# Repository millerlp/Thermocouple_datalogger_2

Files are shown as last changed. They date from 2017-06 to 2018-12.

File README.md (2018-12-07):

## Thermocouple_datalogger_2
### Luke Miller 2017

This repository contains code to run a 8-channel thermocouple
datalogger based on Arduino-type hardware. Currently there are 2 revisions,
A and B, which differ in the type of thermocouple-to-digital chip they use.
Revision A uses the older MAX31855K chip, while Revision B uses the more
recent MAX31856 that effectively superseded the MAX31855 series. Revision A
isn't recommended for new builds. 

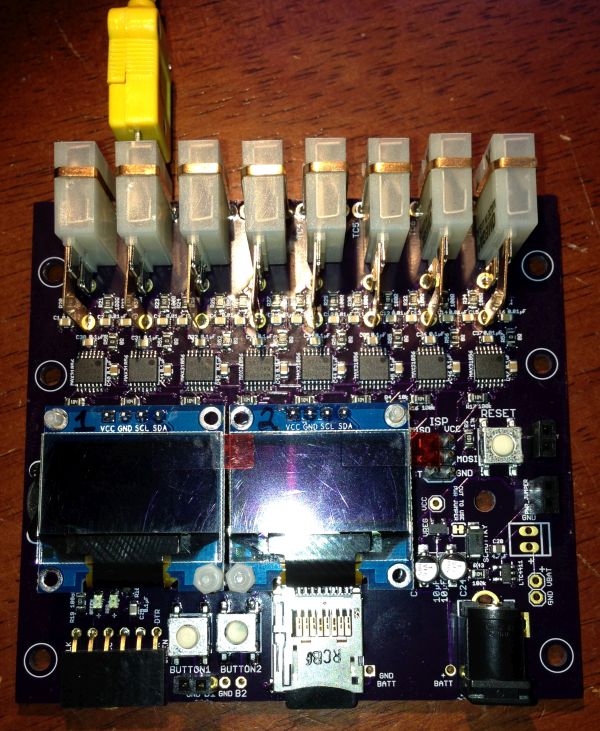
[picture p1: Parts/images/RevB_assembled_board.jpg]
Assembled RevB board


The directory `TempTracker` contains the primary files used to run a 
datalogger board, while the `testing` directory contains various utilities
used to test the basic functions of a datalogger board or to help calibrate
a board. 

## Required libraries:
* https://github.com/millerlp/TClib2
* https://github.com/millerlp/Adafruit_MAX31856 - fork of the original Adafruit_MAX31856 library, mainly changed to return NAN temperature values automatically if there is an error. 
* https://github.com/millerlp/RTClib - to run the onboard real time clock chip DS3231M
* https://github.com/greiman/SdFat - for reading/writing SD cards
* https://github.com/greiman/SSD1306Ascii - for writing to OLED displays

## Hardware designs

Eagle `.sch` and `.brd` design files are provided in the `Eagle_files` directory, along
with images of the designs. 

## Parts list

See the file `Thermocouple_datalogger_parts.xlsx` in the `Parts` directory for a 
list of all of the chips and other parts needed to build a board. There are 
separate sheets for Revision A and B, be careful to use the appropriate sheet. The 
majority of the parts should be available from a single vendor such as Digikey.com,
but the OLED display screens and thermocouple connectors need to be sourced 
elsewhere. 

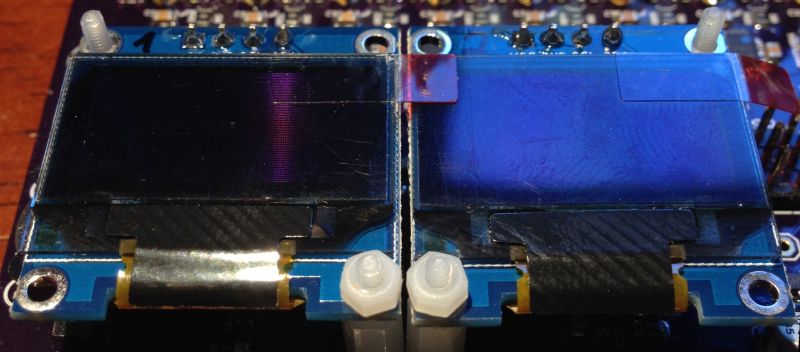
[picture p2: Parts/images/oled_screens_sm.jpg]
oled_screens_sm


For the OLED displays, any 128x64 pixel I2C SSD1306-based board should 
work (typically 0.96" size). These are available from several vendors on sites like
Amazon or Ebay. Be aware that there are I2C and SPI versions available, but this 
datalogger board will only communicate via I2C, so buying the 4-pin I2C version of the
display is sensible.

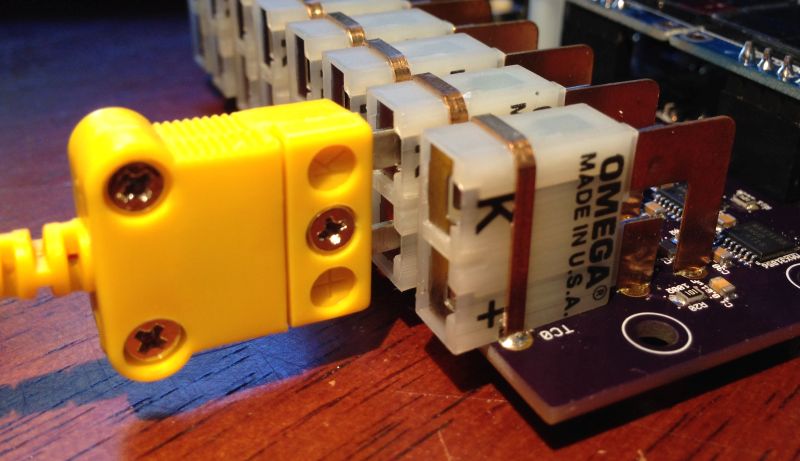
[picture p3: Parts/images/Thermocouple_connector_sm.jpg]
Thermocouple connector


The thermocouple "miniature" connectors will need to be sourced from a 
specialized vendor. The board is designed around Omega Engineering's PCC-SMP-V
connectors, which come in a minimum size batch of 5, so you'll need two batches to 
get 8. If you don't forsee needing to ever unplug a thermocouple, you could solder the
leads directly the board, forgoing the Omega connector. 

## Calibrating
The MAX3185x thermocouple chips are relatively accurate from the factory, and for
most purposes this will be sufficient, if you don't need absolute accuracy less than
1-2C. If you require sub-degree accurracy, calibration will be necessary, and this means
calibrating both the datalogger board and the individual thermocouple leads you use. 

Calibrating the datalogger board actually requires calibrating each of the 8 onboard 
MAX31856 chips separately, using a separate thermocouple calibrator such as the
Omega Engineering CL3515R. These devices are capable of outputting a millivolt signal
equivalent to what the relevant thermocouple type (K, T, J etc) would put out at a
specified temperature. The calibrator comes with a thermocouple cable that plugs 
directly into the thermocouple plugs on the datalogger board, mimicing a real 
thermocouple. The program `Calibration_routine_OLED_RevB` (or the RevA version) is meant
to be used with the external calibrator. After generating a set of calibration data for
a set of known temperatures, you can use the observed temperatures (recorded by the 
datalogger) and the known temperatures (from the calibrator) to fit a straight-line 
regression, and get the intercept (aka offset) and slope of the relationship between 
observed and expected readings. 

The program `Store_calibrations.ino` can then be used 
to upload the full set of 8 offset values and 8 slope values for the 8 MAX3185x 
chips to the datalogger's EEPROM onboard memory. The datalogger board will then have these
calibration values available to use every time it boots up. Typically I find that an 
individual MAX31855K or MAX31856 chip has a slope very near to 1.0 (ideal), but the 
intercept (aka offset) may often be +/- 0.5 to 1C off from ideal (0C offset). Therefore, calibration
is useful if you want the 8 individual channels on a board to be directly comparable to 
each other at the sub-degree level. The nominal temperature resolution of a MAX31855K chip is 0.25C (14-bit A-D converter) and the MAX31856 is 0.0078125 (19-bit A-D converter), but 
chip-to-chip variation from the factory can easily swamp that and only get you 
within +/- 2C of the true temperature in the normal biological range of temperatures. Careful calibration and housing the datalogger board in a thermally stable container 
should get you within 0.1C across channels. 

## Several words about the housing and thermal stability

The thermocouple-to-digital chips rely on an internal temperature sensor in the chip
itself to measure the "cold junction" temperature. This temperature is ideally equivalent
to the temperature at the point where the thermocouple plugs into the board and makes 
the transition from special thermocouple wire to the plain copper of the circuit board
(which is a thermocouple junction by definition). An accurate measurement of the 
distant ("hot") end of the thermocouple probe relies on the MAX3185x chip also knowing 
what the cold junction temperature is quite accurately. If the MAX3185x chip internal
temperature is a few degrees different than the thermocouple plug on the board, the
registered thermocouple temperature will also be off. Ideally, a block of material
that is thermally conductive (an "isothermal block") would be used to connect all 8 
of the MAX3185x chips and their respective thermocouple plugs, and thus keep all of 
those points at the same temperature. A bar of aluminum, copper, or brass, mounted so that 
it sits across the top of all the MAX3185x chips and also rests against the 
thermocouple plug terminals would be best, although these should not all be in 
electrical contact. To thermally couple the various parts without creating short 
circuits, adhesive thermal gap filler (often used to attach heat sinks to circuit 
boards and chips) can be used. This material is electrically non-conductive, but does
a reasonable job of allowing heat to transfer across it, and has the added benefit of
filling small gaps that might exist between an isothermal block and the various parts
due to height differences or variation in how flat the chips sit on the board. The RevB
board has two holes on the edges of the board positioned to help bolt an isothermal 
block across the tops of the MAX31856 chips. 

After provisioning an isothermal block, it would also be useful to then enclose the 
datalogger board in a housing that will stay relatively temperature-stable, or at 
least won't change temperature rapidly at different places. Surrounding the board in
insulating styrofoam may be desirable, and then placing that inside a plastic or metal housing that only exposes the front of the thermocouple connectors to the outside air. 
The RevB board is designed so that panel-mount buttons can be attached to wire leads and 
plugged into the board (via standard 0.1" headers), so that the buttons can be
mounted to a housing. The 2 OLED displays can be attached via 4-wire cables in the 
same manner. The rear/bottom edge of the board (opposite the thermocouple connectors) will 
need to be accessible through a housing wall so that the serial port, micro SD card slot, 
and 2.1mm DC power plug are accessible.

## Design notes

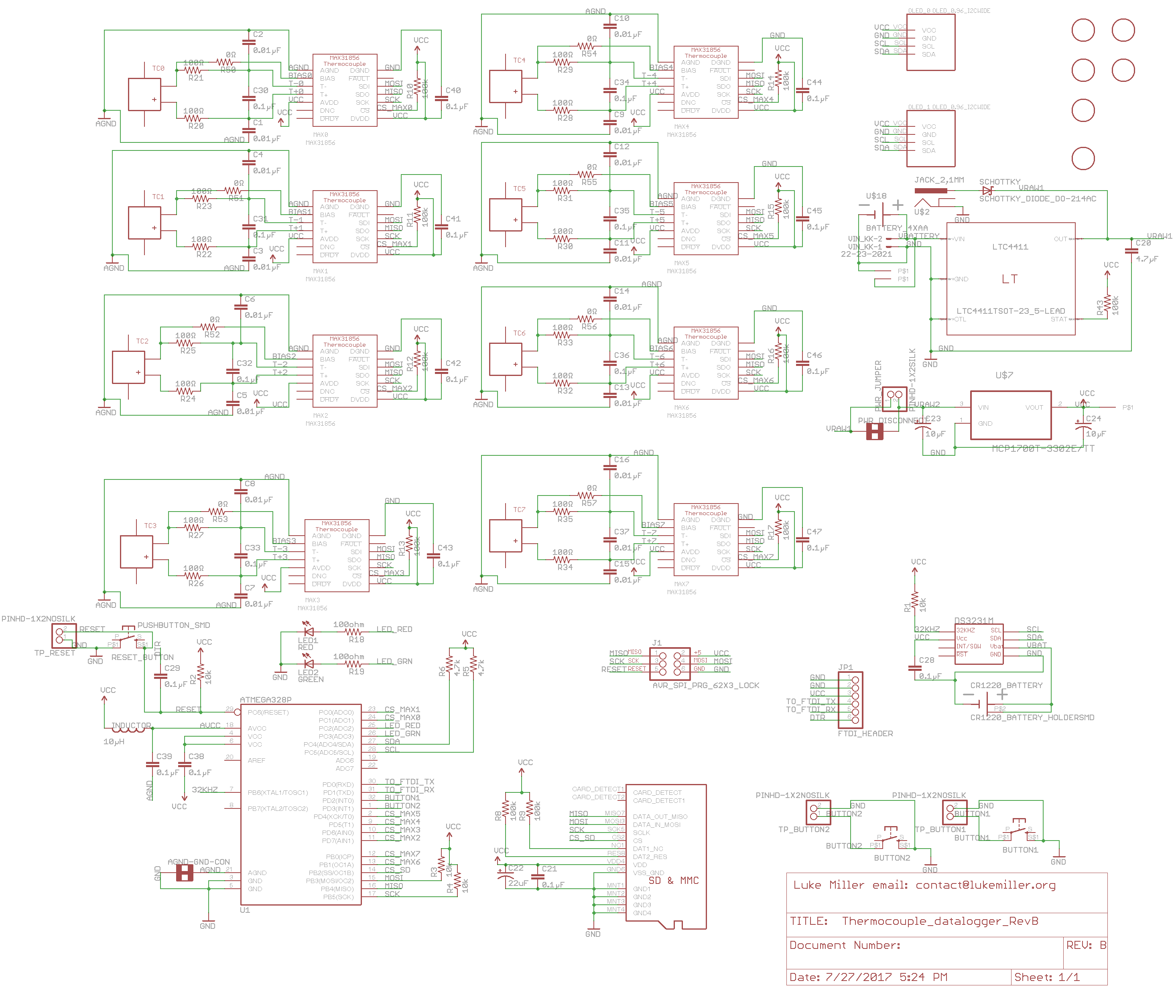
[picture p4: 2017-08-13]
Eagle_files/RevB/Thermocouple_datalogger_RevB_schematic.png

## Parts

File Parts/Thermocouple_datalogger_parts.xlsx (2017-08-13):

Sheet: Thermocouple_datalogger_RevA
Part Description | Eagle library part | Manufacturer | Mfr. PN | Quantity (for 1 board) | Digikey PN | Digikey $ | Extended $
Capacitor, surface mount 10uF 35V, electrolytic, Panasonic FC series, size code B | miller.lbr\CPOL-USB | Panasonic | EEE-FC1C100R | 2 | PCE3995CT-ND | $0.32 | $0.64
Capacitor, 0603 0.01µF 16V ceramic (10000pF) | miller.lbr\CAP0805 | KEMET | C0603C103K4RACTU | 8 | 399-7841-1-ND | $0.28 | $2.24
Capacitor, 0603 0.1µF 16V ceramic | miller.lbr\CAP0805 | KEMET | C0603C104K4RACTU | 13 | 399-1096-1-ND | $0.10 | $1.30
Capacitor, 22µF 6.3V 20% 0805 | miller.lbr\CPOL-US0805 | AVX Corporation | F920J226MPA | 1 | 478-8119-1-ND | $0.43 | $0.43
Resistor, 0603 100ohm | miller.lbr\RESISTOR_SMD | Yageo | RC0603JR-07100RL | 2 | 311-100GRCT-ND | $0.10 | $0.20
Resistor, 0603 10 k ohm | miller.lbr\RESISTOR_SMD | Yageo | RC0603JR-0710KL | 4 | 311-10KGRCT-ND | $0.10 | $0.40
Resistor, 0603 100 k ohm | miller.lbr\RESISTOR_SMD | Yageo | RC0603JR-07100KL | 10 | 311-100KGRCT-ND | $0.10 | $1.00
Screw terminal 2-position, through-hole | miller.lbr\TERMINAL-2PIN-2.54MM | On Shore Technologies | OSTVN02A150 | 2 | ED10561-ND | $0.58 | $1.16
LED, Red 0805 | miller.lbr\LED | Lite-On | LTST-C171KRKT | 1 | 160-1427-1-ND | $0.31 | $0.31
LED, Green 0805 | miller.lbr\LED | Lite-On | LTST-C171GKT | 1 | 160-1423-1-ND | $0.29 | $0.29
MAX31855K thermocouple convertor | miller.lbr\MAX31855 | Maxim Integrated | MAX31855KASA+ | 8 | MAX31855KASA+-ND | $4.50 | $36.00
Pushbutton switch SPST tactile, SMD | miller.lbr\PUSHBUTTON_DPST_SMD | Omron | B3S-1000P | 3 | SW836CT-ND | $0.82 | $2.46
Real Time Clock, DS3231M | miller.lbr\DS3231M | Maxim Integrated | DS3231MZ/V+ | 1 | DS3231MZ/V+-ND | $6.46 | $6.46
CR1220 Battery holder | miller.lbr\CR1220_BATTERY_HOLDER | Keystone | 3000 | 1 | 36-3000-ND | $0.58 | $0.58
CR1220 Battery, lithium |  | Energizer | CR1220VP | 1 | N033-ND | $0.95 | $0.95
4x1 Pin header, female, through hole | miller.lbr\PINHD-1x4BIG_LOCK | Sullins | PPTC041LFBN-RC | 1 | S7002-ND | $0.60 | $0.60
40x1 Pin header, male breakaway |  | Sullins | PRPC040SAAN-RC | 1 | S1011EC-40-ND | $0.74 | $0.74
2x1 Molex KK male connector, through hole | miller.lbr\22-23-2021 | Molex | 22-23-2021 | 1 | WM4200-ND | $0.16 | $0.16
2x1 Molex KK female connector |  | Molex | 10-11-2023 | 1 | WM2601-ND | $0.17 | $0.17
Molex KK crimp-on connector, 24-30AWG |  | Molex | 469990101 | 2 | WM5268-ND | $0.23 | $0.46
Inductor, 10µH 150mA, 360 mOhm | miller.lbr\INDUCTOR0805 | Taiyo-Yuden | LBR2012T100K | 1 | 587-2045-1-ND | $0.11 | $0.11
3x2 Pin header | miller.lbr\AVR_SPI_PRG_6 | Molex | 901310763 | 1 | WM8139-ND | $1.38 | $1.38
Voltage regulator MCP-1700T-3302 3.3V | miller.lbr\MCP1700T-3302E/TT | Microchip | MCP1700T-3302E/TT | 1 | MCP1700T3302ETTCT-ND | $0.38 | $0.38
MicroSD card slot push-push | miller.lbr\MICROSD_MOLEX_REVERSECURRENT | Molex | 5027740891 | 1 | WM24066CT-ND | $3.64 | $3.64
ATmega328P 32-TQFP | miller.lbr\ATMEGA328_SMT | Microchip | ATMEGA328P-AU | 1 | ATMEGA328P-AU-ND | $2.07 | $2.07
2.1mm Power jack | miller.lbr\POWER_JACK_2,1MM | CUI | PJ-202AH | 1 | CP-202AH-ND | $0.74 | $0.74
Ferrite 300 ohm 100Mhz 0805 | miller.lbr\FERRITE_BEAD | TDK | MMZ2012R301AT000 | 16 | 445-2191-1-ND | $0.11 | $1.76
 |  |  |  |  |  | Total | $66.63
Omega miniature thermocouple terminal vertical (5 pack) | miller.lbr\PCC-SMP-THERMOCOUPLE | Omega Engineering | PCC-SMP-V | 2 |  | $21.25 | $42.50

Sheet: Thermocouple_datalogger_RevB
Part Description | Eagle library part | Manufacturer | Mfr. PN | Quantity (for 1 board) | Digikey PN | Digikey $ | Extended $
Capacitor, surface mount 10uF 35V, electrolytic, Panasonic FC series, size code B | miller.lbr\CPOL-USB | Panasonic | EEE-FC1C100R | 2 | PCE3995CT-ND | $0.32 | $0.64
Capacitor, 0805 0.01µF 16V ceramic (10000pF) | miller.lbr\CAP0805 | KEMET | C0809C103K4RACTU | 17 | 399-7995-1-ND | $0.28 | $4.76
Capacitor, 0805 0.1µF 16V ceramic | miller.lbr\CAP0805 | KEMET | C0805C104K4RACTU | 20 | 399-1167-1-ND | $0.12 | $2.40
Capacitor, 0805 4.7µF 25V ceramic X5R | miller.lbr\CAP0805 | KEMET | C0805C475K3PACTU | 1 | 399-5505-1-ND | $0.33 | $0.33
Capacitor, 22µF 6.3V 20% 0805 tantalum | miller.lbr\CPOL-US0805 | AVX Corporation | F920J226MPA | 1 | 478-8119-1-ND | $0.43 | $0.43
Resistor, 0805 0 ohm (jumper) | miller.lbr\RESISTOR_SMD | Yageo | RC0805JR-070RL | 8 | 311-0.0ARCT-ND | $0.10 | $0.80
Resistor, 0805 100ohm 1/8watt | miller.lbr\RESISTOR_SMD | Yageo | RC0805JR-07100RL | 18 | 311-100ARCT-ND | $0.10 | $1.80
Resistor, 0805 4.7k ohm 1/8watt | miller.lbr\RESISTOR_SMD | Yageo | RC0805JR-074K7L | 2 | 311-4.7KARCT-ND | $0.10 | $0.20
Resistor, 0805 10 k ohm 1/8watt | miller.lbr\RESISTOR_SMD | Yageo | RC0805JR-0710KL | 4 | 311-10KARCT-ND | $0.10 | $0.40
Resistor, 0805 100 k ohm 1/8watt | miller.lbr\RESISTOR_SMD | Yageo | RC0805JR-07100KL | 11 | 311-100KARCT-ND | $0.10 | $1.10
LED, Red 0805 | miller.lbr\LED | Lite-On | LTST-C171KRKT | 1 | 160-1427-1-ND | $0.31 | $0.31
LED, Green 0805 | miller.lbr\LED | Lite-On | LTST-C171GKT | 1 | 160-1423-1-ND | $0.29 | $0.29
MAX31856 Thermocouple convertor | miller.lbr\MAX31856 | Maxim Integrated | MAX31856MUD+ | 8 | MAX31856MUD+-ND | $4.41 | $35.28
Pushbutton switch SPST tactile, SMD | miller.lbr\PUSHBUTTON_DPST_SMD | Omron | B3S-1000P | 3 | SW836CT-ND | $0.82 | $2.46
Real Time Clock, DS3231M | miller.lbr\DS3231M | Maxim Integrated | DS3231MZ/V+ | 1 | DS3231MZ/V+-ND | $6.46 | $6.46
CR1220 Battery holder | miller.lbr\CR1220_BATTERY_HOLDER | Keystone | 3000 | 1 | 36-3000-ND | $0.58 | $0.58
CR1220 Battery, lithium |  | Energizer | CR1220VP | 1 | N033-ND | $0.95 | $0.95
4x1 Pin header, female, through hole | miller.lbr\PINHD-1x4BIG_LOCK | Sullins | PPTC041LFBN-RC | 1 | S7002-ND | $0.60 | $0.60
40x1 Pin header, male breakaway |  | Sullins | PRPC040SAAN-RC | 1 | S1011EC-40-ND | $0.74 | $0.74
2x1 Molex KK male connector, through hole | miller.lbr\22-23-2021 | Molex | 22-23-2021 | 1 | WM4200-ND | $0.16 | $0.16
2x1 Molex KK female connector |  | Molex | 10-11-2023 | 1 | WM2601-ND | $0.17 | $0.17
Molex KK crimp-on connector, 24-30AWG |  | Molex | 469990101 | 2 | WM5268-ND | $0.23 | $0.46
Inductor, 10µH 150mA, 360 mOhm | miller.lbr\INDUCTOR0805 | Taiyo-Yuden | LBR2012T100K | 1 | 587-2045-1-ND | $0.11 | $0.11
3x2 Pin header | miller.lbr\AVR_SPI_PRG_6 | Molex | 901310763 | 1 | WM8139-ND | $1.38 | $1.38
Voltage regulator MCP-1700T-3302 3.3V | miller.lbr\MCP1700T-3302E/TT | Microchip | MCP1700T-3302E/TT | 1 | MCP1700T3302ETTCT-ND | $0.38 | $0.38
MicroSD card slot push-push | miller.lbr\MICROSD_MOLEX_REVERSECURRENT | Molex | 5027740891 | 1 | WM24066CT-ND | $3.64 | $3.64
ATmega328P 32-TQFP | miller.lbr\ATMEGA328_SMT | Microchip | ATMEGA328P-AU | 1 | ATMEGA328P-AU-ND | $2.07 | $2.07
2.1mm Power jack | miller.lbr\POWER_JACK_2,1MM | CUI | PJ-202AH | 1 | CP-202AH-ND | $0.74 | $0.74
Schottky diode 20V 1A | miller.lbr\SCHOTTKY_DIODE_DO-214AC | Vishay Semiconductor | SS12-E3/61T | 1 | SS12-E3/61TGICT-ND | $0.40 | $0.40
AA battery holder 4xAA, through hole | miller.lbr\BATTERY_4XAA | Keystone | 2477 | 1 | 36-2477-ND | $2.23 | $2.23
Power path controller LTC4411 TSOT-23 | miller.lbr\LTC4411TSOT-23_5-LEAD | Linear Technology | LTC4411ES5 | 1 | LTC4411ES5#TRMPBFCT-ND | $3.88 | $3.88
 |  |  |  |  |  | Digikey Total | $76.15
Other Vendors
Omega miniature thermocouple terminal vertical (5 pack) | miller.lbr\PCC-SMP-THERMOCOUPLE | Omega Engineering | PCC-SMP-V | 2 |  | $21.25 | $42.50
OLED 0.96" I2C screen 128x64 4pin | miller.lbr\OLED_0.96_I2CWIDE | Amazon HiLetgo | 3-01-1234-IIC-W | 2 | http://a.co/hNL97jw | $8.88 | $17.76

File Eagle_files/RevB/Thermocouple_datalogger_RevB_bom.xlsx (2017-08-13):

Qty | Value | Device | Parts
2 |  | PUSHBUTTON_DPST_SMDSTANDARD | BUTTON1, BUTTON2
17 | 0.01µF | CAP0805 | C1, C2, C3, C4, C5, C6, C7, C9, C10, C11, C12, C13, C14, C15, C16, C17, C37
20 | 0.1µF | CAP0805 | C30, C31, C32, C33, C34, C35, C36, C40, C41, C42, C43, C44, C45, C46, C47, C48, C49, C51, C52, C54
8 | 0O | RESISTOR_SMDR0805 | R7, R24, R27, R30, R33, R36, R39, R42
11 | 100k | RESISTOR_SMDR0805 | R10, R11, R12, R13, R14, R15, R16, R17, R18, R19, R43
2 | 100ohm | RESISTOR_SMDR0805 | R8, R9
16 | 100O | RESISTOR_SMDR0805 | R5, R6, R22, R23, R25, R26, R28, R29, R31, R32, R34, R35, R37, R38, R40, R41
4 | 10k | RESISTOR_SMDR0805 | R1, R2, R20, R21
2 | 10µF | CPOL-USB | C23, C24
1 | 10µH | INDUCTOR0805_TY | INDUCTOR
1 | 22-23-2021 | 22-23-2021 | VIN_KK
1 | 22uF | CPOL-US0805 | C8
2 | 4.7k | RESISTOR_SMDR0805 | R3, R4
1 | 4.7µF | CAP0805 | C18
1 | ATMEGA328P | ATMEGA328_SMT | U1
1 | AVR_SPI_PRG_62X3_LOCK | AVR_SPI_PRG_62X3_LOCK | J1
1 | BATTERY_4XAA | BATTERY_4XAA | U$18
1 | CR1220_BATTERY_HOLDERSMD | CR1220_BATTERY_HOLDERSMD | CR1220_BATTERY
1 | DS3231MSOIC-8 | DS3231MSOIC-8 | DS3231M
1 | FTDI_HEADER | PINHD-1X6RA | JP1
1 | GREEN | LED0805 | LED2
6 | HOLE-LAYOUT4-40-SOCKET-HEAD | HOLE-LAYOUT4-40-SOCKET-HEAD | U$6, U$15, U$16, U$23, U$24, U$25
1 | JACK_2,1MM | POWER_JACK_2,1MM | U$2
1 | LTC4411TSOT-23_5-LEAD | LTC4411TSOT-23_5-LEAD | LTC4411
8 | MAX31856 | MAX31856 | MAX0, MAX1, MAX2, MAX3, MAX4, MAX5, MAX6, MAX7
1 | MCP1700T-3302E/TT | MCP1700T-3302E/TT | U$7
1 | MICROSD_MOLEX_REVERSECURRENT | MICROSD_MOLEX_REVERSECURRENT | U$5
2 | OLED_0.96_I2CWIDE | OLED_0.96_I2CWIDE | OLED_0, OLED_1
8 | PCC-SMP-THERMOCOUPLEVERTICAL | PCC-SMP-THERMOCOUPLEVERTICAL | TC0, TC1, TC2, TC3, TC4, TC5, TC6, TC7
3 | PINHD-1X1STANDARD | PINHD-1X1STANDARD | TP_GND, TP_VBAT, VCC
3 | PINHD-1X2NOSILK | PINHD-1X2NOSILK | TP_BUTTON1, TP_BUTTON2, TP_RESET
1 | PUSHBUTTON_SMD | PUSHBUTTON_DPST_SMDSTANDARD | RESET_BUTTON
1 | RED | LED0805 | LED1
1 | SCHOTTKY_DIODE_DO-214AC | SCHOTTKY_DIODE_DO-214AC | SCHOTTKY
1 | SOLDER_JUMPER_TRACESTANDARD | SOLDER_JUMPER_TRACESTANDARD | AGND-GND-CON

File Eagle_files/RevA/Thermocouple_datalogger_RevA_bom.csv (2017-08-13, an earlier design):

Thermocouple_datalogger_RevA 2017-06-01
Part | Value | Device | Package | Description
AGND-GND-CON | SOLDER_JUMPER_TRACESTANDARD | SOLDER_JUMPER_TRACESTANDARD | SJ_2S-TRACE | Solder jumper with trace
BUTTON1 |  | PUSHBUTTON_DPST_SMDSTANDARD | PUSHBUTTON_DPST_SMD | PUSHBUTTON DPST SMD
BUTTON2 |  | PUSHBUTTON_DPST_SMDSTANDARD | PUSHBUTTON_DPST_SMD | PUSHBUTTON DPST SMD
C8 | 22uF | CPOL-US0805 | C0805_POL | POLARIZED CAPACITOR, American symbol
C23 | 10µF | CPOL-USB | PANASONIC_B | POLARIZED CAPACITOR, American symbol
C24 | 10µF | CPOL-USB | PANASONIC_B | POLARIZED CAPACITOR, American symbol
C30 | 0.01µF | CAP0805 | 805 | Capacitor
C31 | 0.01µF | CAP0805 | 805 | Capacitor
C32 | 0.01µF | CAP0805 | 805 | Capacitor
C33 | 0.01µF | CAP0805 | 805 | Capacitor
C34 | 0.01µF | CAP0805 | 805 | Capacitor
C35 | 0.01µF | CAP0805 | 805 | Capacitor
C36 | 0.01µF | CAP0805 | 805 | Capacitor
C37 | 0.01µF | CAP0805 | 805 | Capacitor
C40 | 0.1µF | CAP0805 | 805 | Capacitor
C41 | 0.1µF | CAP0805 | 805 | Capacitor
C42 | 0.1µF | CAP0805 | 805 | Capacitor
C43 | 0.1µF | CAP0805 | 805 | Capacitor
C44 | 0.1µF | CAP0805 | 805 | Capacitor
C45 | 0.1µF | CAP0805 | 805 | Capacitor
C46 | 0.1µF | CAP0805 | 805 | Capacitor
C47 | 0.1µF | CAP0805 | 805 | Capacitor
C48 | 0.1µF | CAP0805 | 805 | Capacitor
C49 | 0.1µF | CAP0805 | 805 | Capacitor
C51 | 0.1µF | CAP0805 | 805 | Capacitor
C52 | 0.1µF | CAP0805 | 805 | Capacitor
C54 | 0.1µF | CAP0805 | 805 | Capacitor
CR1220_BATTERY | CR1220_BATTERY_HOLDERSMD | CR1220_BATTERY_HOLDERSMD | CR1220_BATTERY_HOLDER_SMD | CR1220 Battery Holder
DIGITAL_OUTPUT_0 | TERMINAL-2PIN-2.54MM | TERMINAL-2PIN-2.54MM | TERMINAL-2PIN-2.54MM | Terminal block 0.1 spacing"
DIGITAL_OUTPUT_1 | TERMINAL-2PIN-2.54MM | TERMINAL-2PIN-2.54MM | TERMINAL-2PIN-2.54MM | Terminal block 0.1 spacing"
DS3231M | DS3231MSOIC-8 | DS3231MSOIC-8 | DS3231M_SOIC8 | DS3231M real time clock
INDUCTOR | 10µH | INDUCTOR0805_TY | I_0805 | Inductor
J1 | AVR_SPI_PRG_62X3_LOCK | AVR_SPI_PRG_62X3_LOCK | 2X3_LOCK | AVR ISP 6 Pin
JP1 | FTDI_HEADER | PINHD-1X6LOCK | 1X06-BIGLOCK | PIN HEADER
LED1 | RED | LED0805 | CHIPLED_0805 | LEDs
LED2 | GREEN | LED0805 | CHIPLED_0805 | LEDs
MAX0 | MAX31855 | MAX31855 | SO08 | MAX31855 Thermocouple amplifier with cold junction compensation, SPI communication
MAX1 | MAX31855 | MAX31855 | SO08 | MAX31855 Thermocouple amplifier with cold junction compensation, SPI communication
MAX2 | MAX31855 | MAX31855 | SO08 | MAX31855 Thermocouple amplifier with cold junction compensation, SPI communication
MAX3 | MAX31855 | MAX31855 | SO08 | MAX31855 Thermocouple amplifier with cold junction compensation, SPI communication
MAX4 | MAX31855 | MAX31855 | SO08 | MAX31855 Thermocouple amplifier with cold junction compensation, SPI communication
MAX5 | MAX31855 | MAX31855 | SO08 | MAX31855 Thermocouple amplifier with cold junction compensation, SPI communication
MAX6 | MAX31855 | MAX31855 | SO08 | MAX31855 Thermocouple amplifier with cold junction compensation, SPI communication
MAX7 | MAX31855 | MAX31855 | SO08 | MAX31855 Thermocouple amplifier with cold junction compensation, SPI communication
OLED_0 | OLED_0.96_I2CVCC_PIN1 | OLED_0.96_I2CVCC_PIN1 | OLED_0.96_I2C_VCC_PIN1 | CHECK VCC & GND PIN VARIANT
OLED_1 | OLED_0.96_I2CVCC_PIN1 | OLED_0.96_I2CVCC_PIN1 | OLED_0.96_I2C_VCC_PIN1 | CHECK VCC & GND PIN VARIANT
R1 | 10k | RESISTOR_SMDR0805 | R0805 | RESISTOR, American symbol
R2 | 10k | RESISTOR_SMDR0805 | R0805 | RESISTOR, American symbol
R3 | 10k | RESISTOR_SMDR0805 | R0805 | RESISTOR, American symbol
R4 | 10k | RESISTOR_SMDR0805 | R0805 | RESISTOR, American symbol
R8 | 100ohm | RESISTOR_SMDR0805 | R0805 | RESISTOR, American symbol
R9 | 100ohm | RESISTOR_SMDR0805 | R0805 | RESISTOR, American symbol
R10 | 100k | RESISTOR_SMDR0805 | R0805 | RESISTOR, American symbol
R11 | 100k | RESISTOR_SMDR0805 | R0805 | RESISTOR, American symbol
R12 | 100k | RESISTOR_SMDR0805 | R0805 | RESISTOR, American symbol
R13 | 100k | RESISTOR_SMDR0805 | R0805 | RESISTOR, American symbol
R14 | 100k | RESISTOR_SMDR0805 | R0805 | RESISTOR, American symbol
R15 | 100k | RESISTOR_SMDR0805 | R0805 | RESISTOR, American symbol
R16 | 100k | RESISTOR_SMDR0805 | R0805 | RESISTOR, American symbol
R17 | 100k | RESISTOR_SMDR0805 | R0805 | RESISTOR, American symbol
R18 | 100k | RESISTOR_SMDR0805 | R0805 | RESISTOR, American symbol
R19 | 100k | RESISTOR_SMDR0805 | R0805 | RESISTOR, American symbol
RESET_BUTTON | PUSHBUTTON_SMD | PUSHBUTTON_DPST_SMDSTANDARD | PUSHBUTTON_DPST_SMD | PUSHBUTTON DPST SMD
TC0 | PCC-SMP-THERMOCOUPLEVERTICAL | PCC-SMP-THERMOCOUPLEVERTICAL | PCC-SMP-V | PCC-SMP
TC1 | PCC-SMP-THERMOCOUPLEVERTICAL | PCC-SMP-THERMOCOUPLEVERTICAL | PCC-SMP-V | PCC-SMP
TC2 | PCC-SMP-THERMOCOUPLEVERTICAL | PCC-SMP-THERMOCOUPLEVERTICAL | PCC-SMP-V | PCC-SMP
TC3 | PCC-SMP-THERMOCOUPLEVERTICAL | PCC-SMP-THERMOCOUPLEVERTICAL | PCC-SMP-V | PCC-SMP
TC4 | PCC-SMP-THERMOCOUPLEVERTICAL | PCC-SMP-THERMOCOUPLEVERTICAL | PCC-SMP-V | PCC-SMP
TC5 | PCC-SMP-THERMOCOUPLEVERTICAL | PCC-SMP-THERMOCOUPLEVERTICAL | PCC-SMP-V | PCC-SMP
TC6 | PCC-SMP-THERMOCOUPLEVERTICAL | PCC-SMP-THERMOCOUPLEVERTICAL | PCC-SMP-V | PCC-SMP
TC7 | PCC-SMP-THERMOCOUPLEVERTICAL | PCC-SMP-THERMOCOUPLEVERTICAL | PCC-SMP-V | PCC-SMP
U$2 | JACK_2,1MM | POWER_JACK_2,1MM | POWER_JACK_DC_2,1MM | DC Power Jack, 2.1mm center pin.
U$3 | Ferrite300ohm100MHz | FERRITE_BEAD0805 | 805 | Ferrite bead
U$4 | Ferrite300ohm100MHz | FERRITE_BEAD0805 | 805 | Ferrite bead
U$5 | MICROSD_MOLEX_REVERSECURRENT | MICROSD_MOLEX_REVERSECURRENT | MICROSD_SOCKET_MOLEX_REVERSEMOUNT | Molex micro SD connector, push-push spring loaded, reverse" mount"
U$6 | HOLE-LAYOUT4-40-SOCKET-HEAD | HOLE-LAYOUT4-40-SOCKET-HEAD | 4-40-SCREW-HOLE | Drill hole
U$7 | MCP1700T-3302E/TT | MCP1700T-3302E/TT | SOT95P237X112-3N | Low Quiescent Current LDO
U$9 | Ferrite300ohm100MHz | FERRITE_BEAD0805 | 805 | Ferrite bead
U$10 | Ferrite300ohm100MHz | FERRITE_BEAD0805 | 805 | Ferrite bead
U$11 | Ferrite300ohm100MHz | FERRITE_BEAD0805 | 805 | Ferrite bead
U$12 | Ferrite300ohm100MHz | FERRITE_BEAD0805 | 805 | Ferrite bead
U$13 | Ferrite300ohm100MHz | FERRITE_BEAD0805 | 805 | Ferrite bead
U$14 | Ferrite300ohm100MHz | FERRITE_BEAD0805 | 805 | Ferrite bead
U$15 | Ferrite300ohm100MHz | FERRITE_BEAD0805 | 805 | Ferrite bead
U$16 | Ferrite300ohm100MHz | FERRITE_BEAD0805 | 805 | Ferrite bead
U$17 | Ferrite300ohm100MHz | FERRITE_BEAD0805 | 805 | Ferrite bead
U$18 | Ferrite300ohm100MHz | FERRITE_BEAD0805 | 805 | Ferrite bead
U$19 | Ferrite300ohm100MHz | FERRITE_BEAD0805 | 805 | Ferrite bead
U$20 | Ferrite300ohm100MHz | FERRITE_BEAD0805 | 805 | Ferrite bead
U$21 | Ferrite300ohm100MHz | FERRITE_BEAD0805 | 805 | Ferrite bead
U$22 | Ferrite300ohm100MHz | FERRITE_BEAD0805 | 805 | Ferrite bead
U$23 | HOLE-LAYOUT4-40-SOCKET-HEAD | HOLE-LAYOUT4-40-SOCKET-HEAD | 4-40-SCREW-HOLE | Drill hole
U$24 | HOLE-LAYOUT4-40-SOCKET-HEAD | HOLE-LAYOUT4-40-SOCKET-HEAD | 4-40-SCREW-HOLE | Drill hole
U$25 | HOLE-LAYOUT4-40-SOCKET-HEAD | HOLE-LAYOUT4-40-SOCKET-HEAD | 4-40-SCREW-HOLE | Drill hole
U1 | ATMEGA328P | ATMEGA328_SMT | TQFP32-08 | 32-Pin Atmega328
VIN_KK | 22-23-2021 | 22-23-2021 | 22-23-2021 | Molex KK series

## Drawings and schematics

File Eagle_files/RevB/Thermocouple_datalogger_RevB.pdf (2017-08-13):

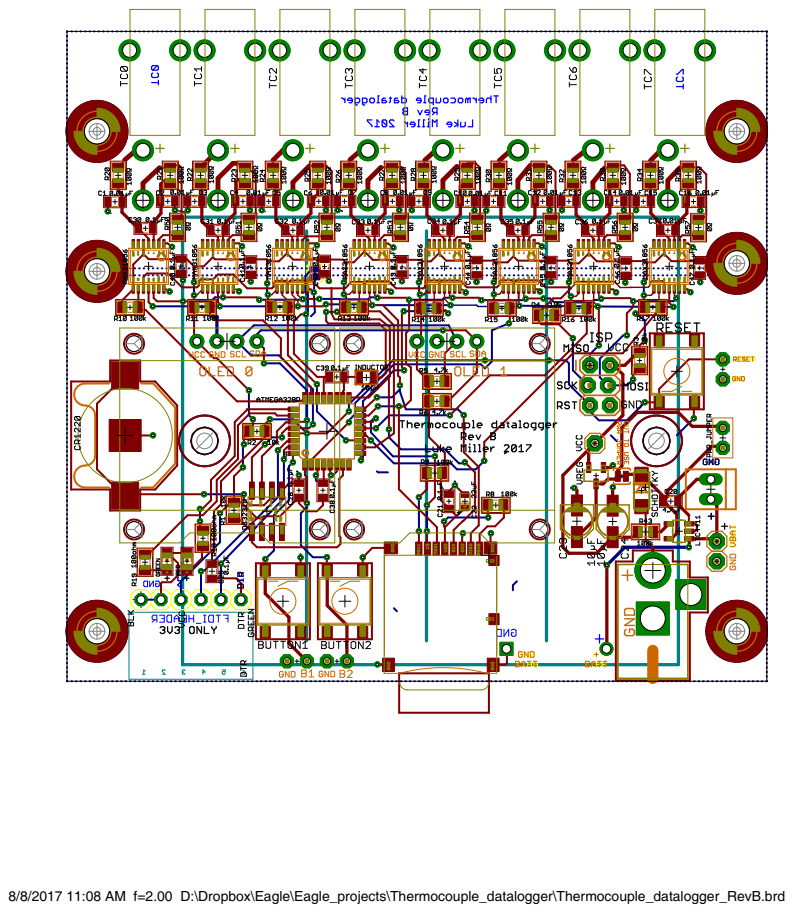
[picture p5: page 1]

8/8/2017 11:08 AM f=2.00 D:\Dropbox\Eagle\Eagle_projects\Thermocouple_datalogger\Thermocouple_datalogger_RevB.brd

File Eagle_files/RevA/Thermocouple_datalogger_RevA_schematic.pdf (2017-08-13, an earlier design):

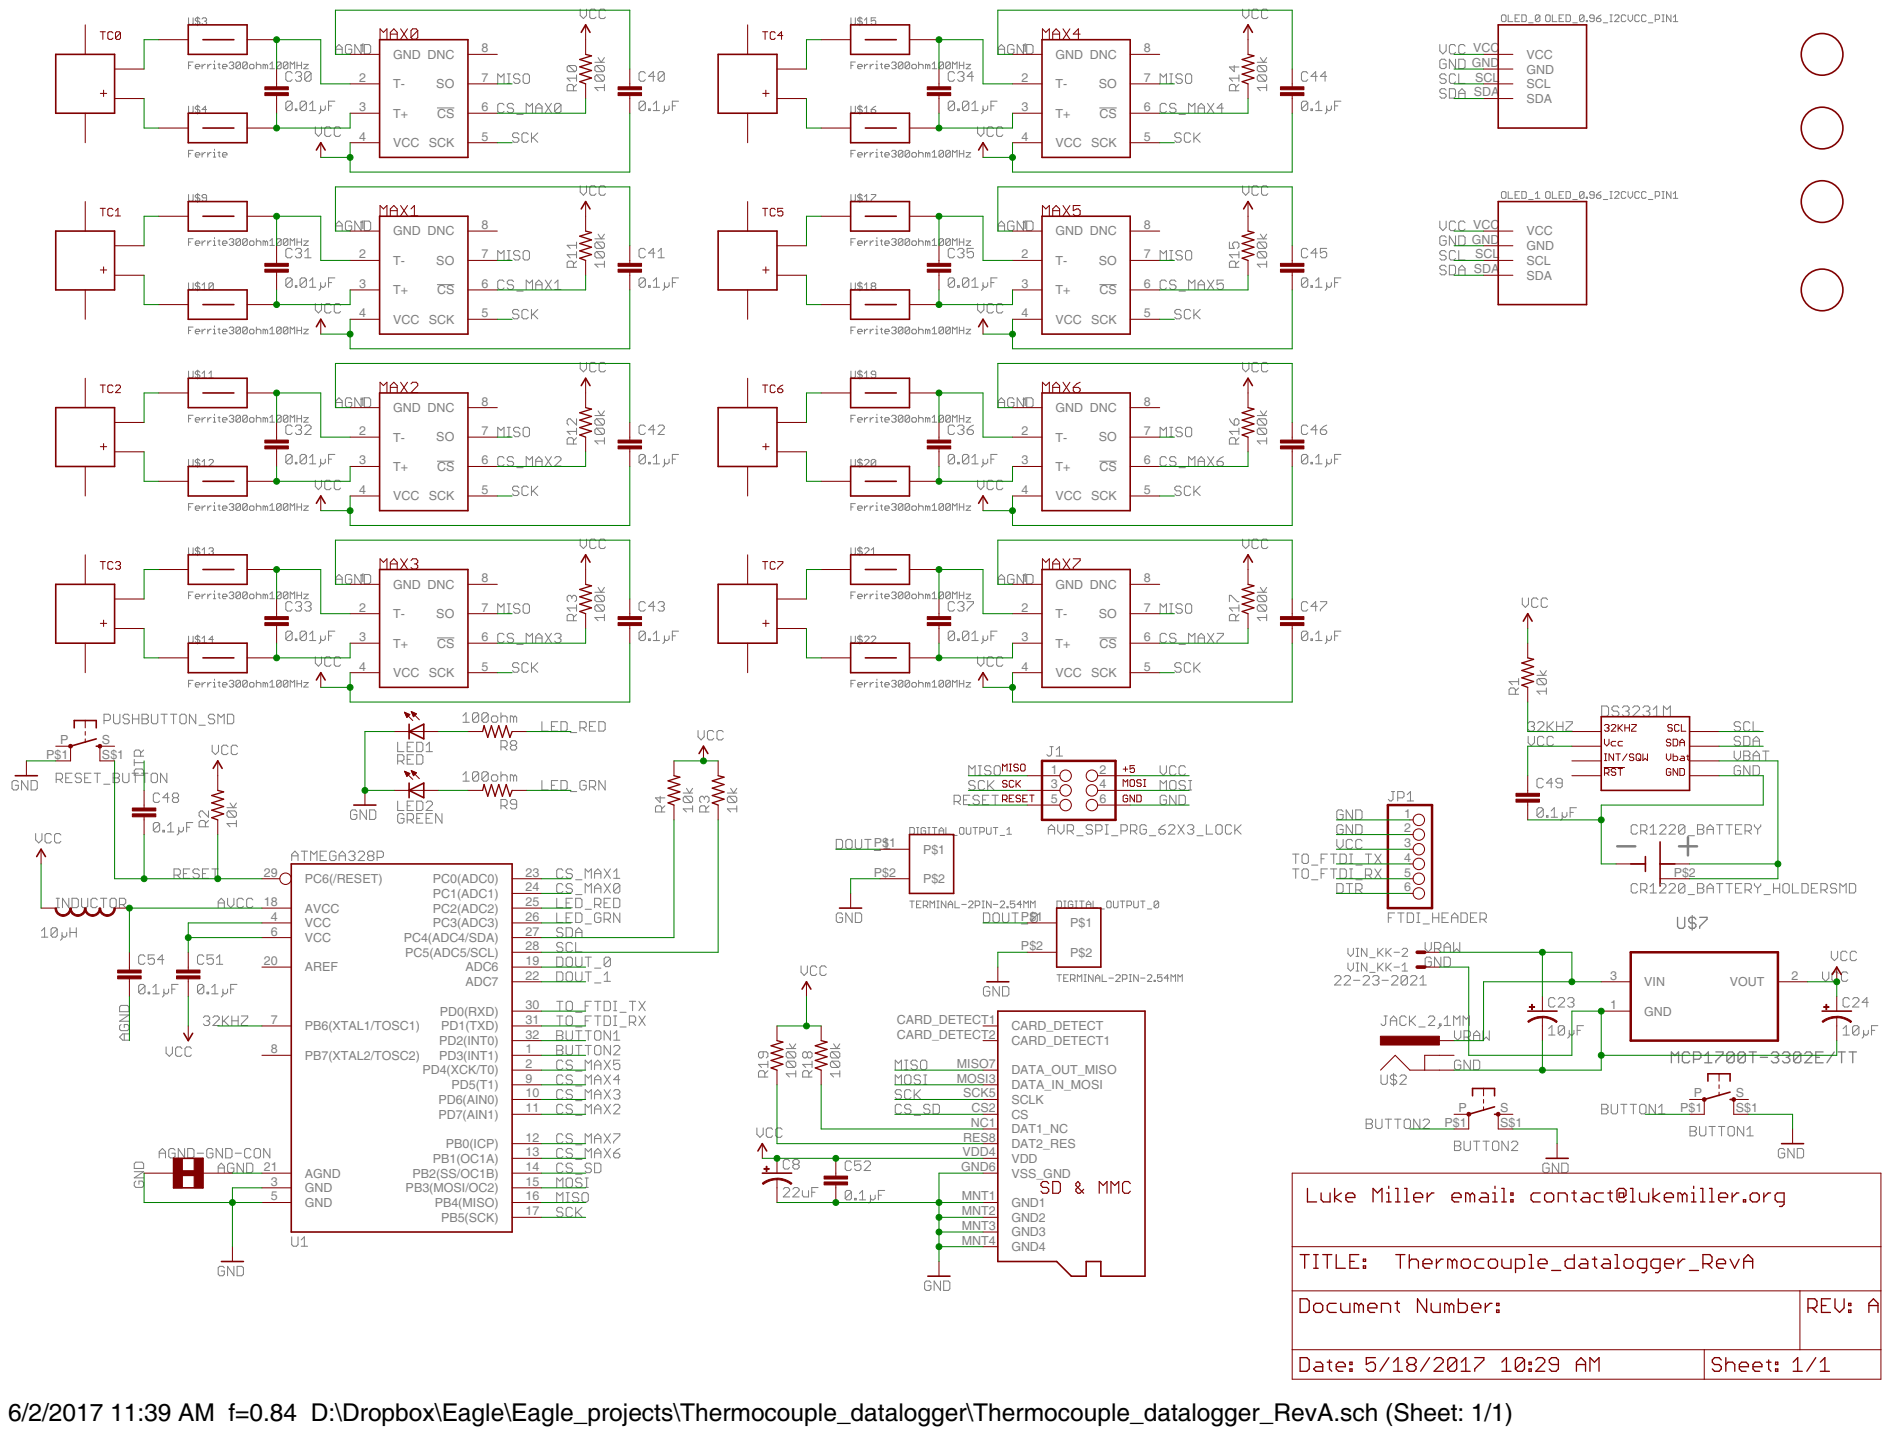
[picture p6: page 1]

6/2/2017 11:39 AM f=0.84 D:\Dropbox\Eagle\Eagle_projects\Thermocouple_datalogger\Thermocouple_datalogger_RevA.sch (Sheet: 1/1)

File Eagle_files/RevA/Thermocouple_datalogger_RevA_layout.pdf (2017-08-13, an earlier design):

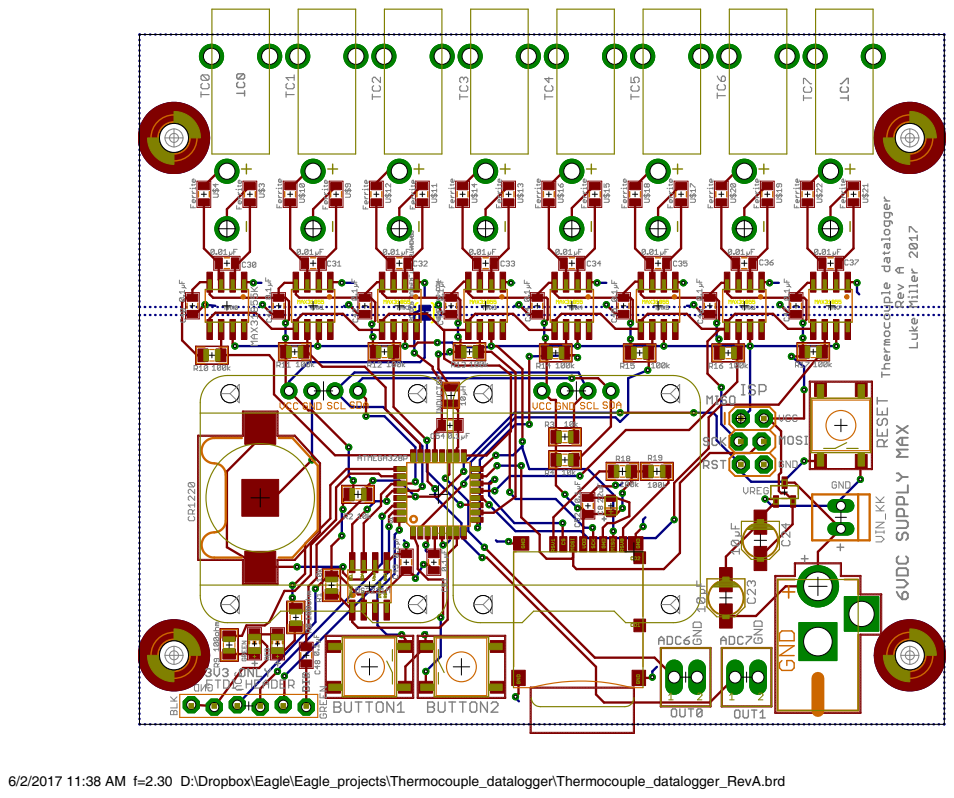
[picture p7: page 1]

6/2/2017 11:38 AM f=2.30 D:\Dropbox\Eagle\Eagle_projects\Thermocouple_datalogger\Thermocouple_datalogger_RevA.brd

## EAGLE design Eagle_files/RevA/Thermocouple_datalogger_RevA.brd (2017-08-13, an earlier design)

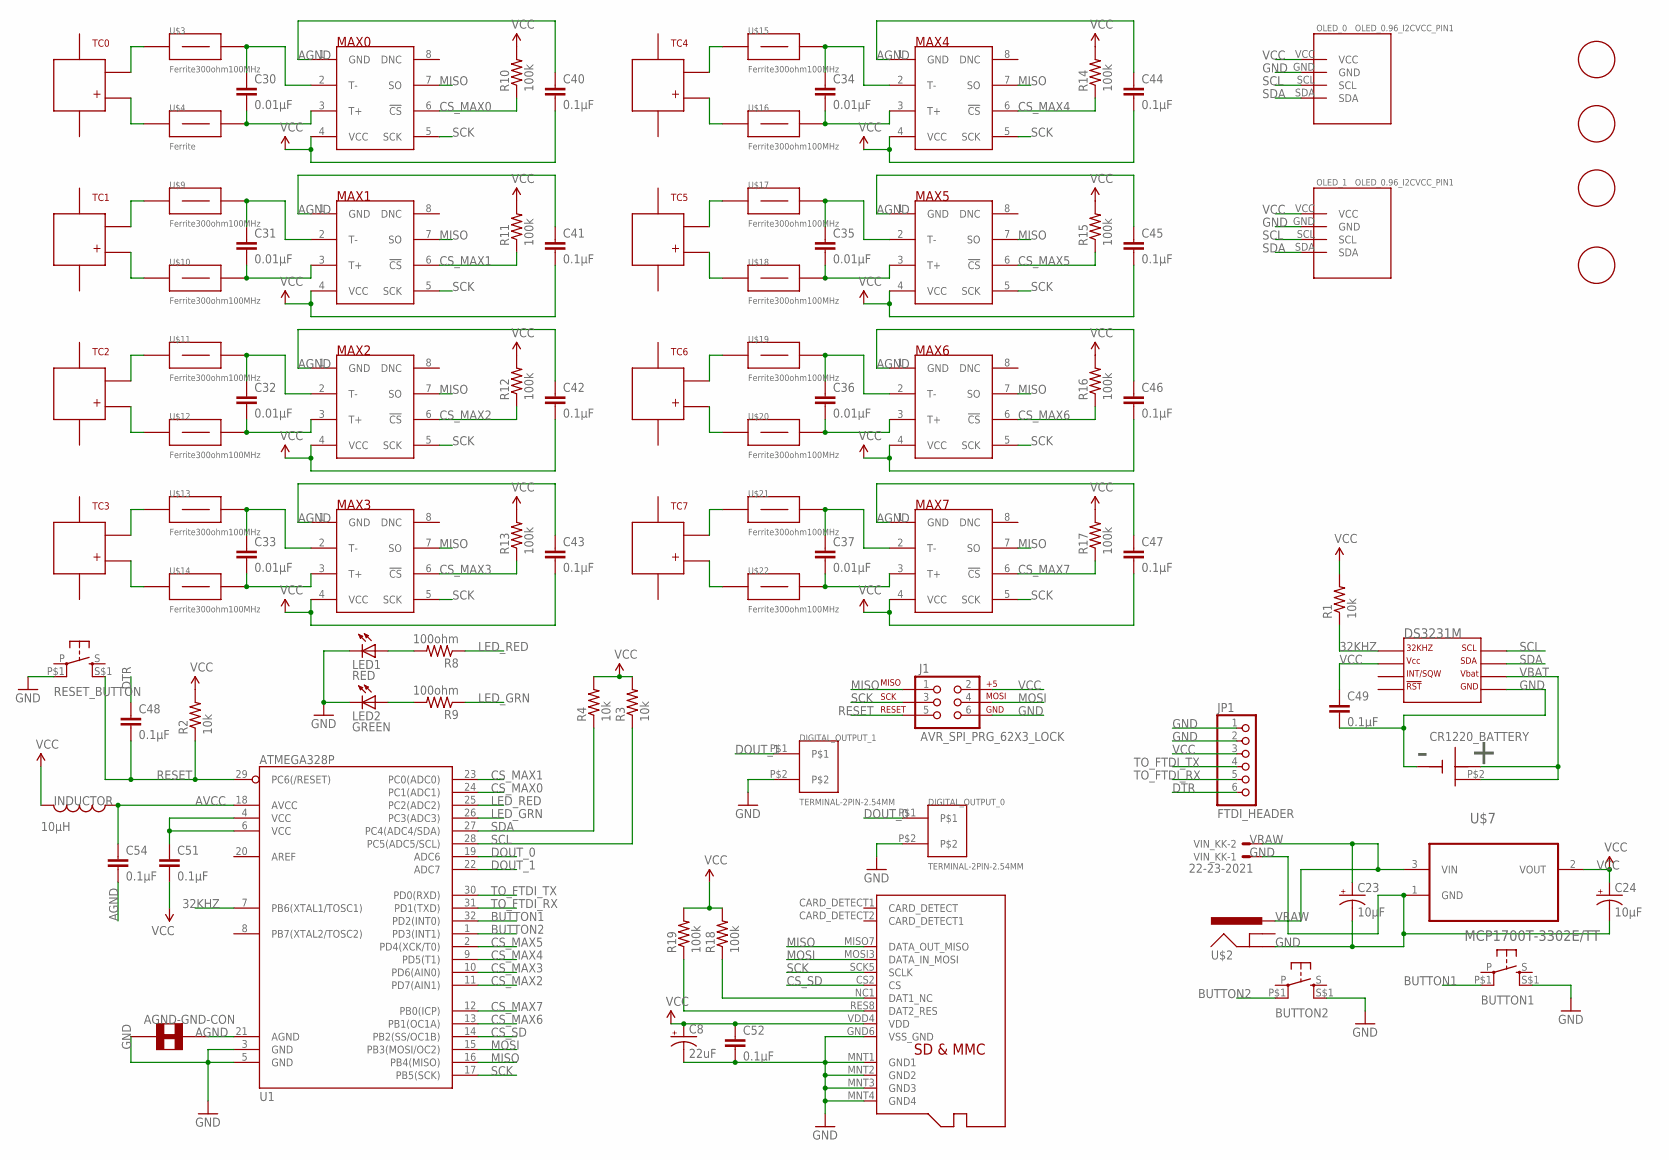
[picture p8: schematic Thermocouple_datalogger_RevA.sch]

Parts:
AGND-GND-CON: SOLDER_JUMPER_TRACESTANDARD; SJ_2S-TRACE
BUTTON1, BUTTON2: PUSHBUTTON_DPST_SMDSTANDARD; PUSHBUTTON_DPST_SMD
C8: 22uF; C0805_POL
C23, C24: 10µF; PANASONIC_B
C30, C31, C32, C33, C34, C35, C36, C37: 0.01µF; 0805
C40, C41, C42, C43, C44, C45, C46, C47, C48, C49, C51, C52, C54: 0.1µF; 0805
CR1220_BATTERY: CR1220_BATTERY_HOLDERSMD; CR1220_BATTERY_HOLDER_SMD
DIGITAL_OUTPUT_0, DIGITAL_OUTPUT_1: TERMINAL-2PIN-2.54MM
DS3231M: DS3231MSOIC-8; DS3231M_SOIC8
INDUCTOR: 10µH; I_0805
J1: AVR_SPI_PRG_62X3_LOCK; 2X3_LOCK
JP1: FTDI_HEADER; 1X06-BIGLOCK
LED1: RED; CHIPLED_0805
LED2: GREEN; CHIPLED_0805
MAX0, MAX1, MAX2, MAX3, MAX4, MAX5, MAX6, MAX7: MAX31855; SO08
OLED_0, OLED_1: OLED_0.96_I2CVCC_PIN1; OLED_0.96_I2C_VCC_PIN1
R1, R2, R3, R4: 10k; R0805
R8, R9: 100ohm; R0805
R10, R11, R12, R13, R14, R15, R16, R17, R18, R19: 100k; R0805
RESET_BUTTON: PUSHBUTTON_SMD; PUSHBUTTON_DPST_SMD
TC0, TC1, TC2, TC3, TC4, TC5, TC6, TC7: PCC-SMP-THERMOCOUPLEVERTICAL; PCC-SMP-V
U1: ATMEGA328P; TQFP32-08
U$2: JACK_2,1MM; POWER_JACK_DC_2,1MM
U$3, U$9, U$10, U$11, U$12, U$13, U$14, U$15, U$16, U$17, U$18, U$19, U$20, U$21, U$22: Ferrite300ohm100MHz; 0805
U$4: Ferrite; 0805
U$5: MICROSD_MOLEX_REVERSECURRENT; MICROSD_SOCKET_MOLEX_REVERSEMOUNT
U$6, U$23, U$24, U$25: HOLE-LAYOUT4-40-SOCKET-HEAD; 4-40-SCREW-HOLE
U$7: MCP1700T-3302E/TT; SOT95P237X112-3N
VIN_KK: 22-23-2021

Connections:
32KHZ: DS3231M.1 (P$1_32KHZ), R1.1, U1.7 (PB6(XTAL1/TOSC1))
AGND: AGND-GND-CON.2, C40.1, C41.1, C42.1, C43.1, C44.1, C45.1, C46.1, C47.1, C54.2, MAX0.1 (GND), MAX1.1 (GND), MAX2.1 (GND), MAX3.1 (GND), MAX4.1 (GND), MAX5.1 (GND), MAX6.1 (GND), MAX7.1 (GND), U1.21 (AGND)
AVCC: C54.1, INDUCTOR.P$1 (1), U1.18 (AVCC)
BUTTON1: BUTTON1.P$1 (P1), U1.32 (PD2(INT0))
BUTTON2: BUTTON2.P$1 (P1), U1.1 (PD3(INT1))
CS_MAX0: MAX0.6 (!CS), R10.1, U1.24 (PC1(ADC1))
CS_MAX1: MAX1.6 (!CS), R11.1, U1.23 (PC0(ADC0))
CS_MAX2: MAX2.6 (!CS), R12.1, U1.11 (PD7(AIN1))
CS_MAX3: MAX3.6 (!CS), R13.1, U1.10 (PD6(AIN0))
CS_MAX4: MAX4.6 (!CS), R14.1, U1.9 (PD5(T1))
CS_MAX5: MAX5.6 (!CS), R15.1, U1.2 (PD4(XCK/T0))
CS_MAX6: MAX6.6 (!CS), R16.1, U1.13 (PB1(OC1A))
CS_MAX7: MAX7.6 (!CS), R17.1, U1.12 (PB0(ICP))
CS_SD: U1.14 (PB2(SS/OC1B)), U$5.CS2 (CS)
DOUT_0: DIGITAL_OUTPUT_0.P$1, U1.19 (ADC6)
DOUT_1: DIGITAL_OUTPUT_1.P$1, U1.22 (ADC7)
DTR: C48.1, JP1.6
GND: AGND-GND-CON.1, BUTTON1.S$1 (S1), BUTTON2.S$1 (S1), C8.P$2_C (-), C23.-, C24.-, C49.2, C52.2, CR1220_BATTERY.GND, DIGITAL_OUTPUT_0.P$2, DIGITAL_OUTPUT_1.P$2, DS3231M.5 (P$5_GND), J1.6, JP1.1, JP1.2, LED1.C, LED2.C, OLED_0.GND, OLED_1.GND, RESET_BUTTON.P$1 (P1), U1.3 (GND), U1.5 (GND), U$2.P$2 (GND), U$5.GND6 (VSS_GND), U$5.MNT1 (GND1), U$5.MNT2 (GND2), U$5.MNT3 (GND3), U$5.MNT4 (GND4), U$7.1 (GND), VIN_KK.1
LED_GRN: R9.1, U1.26 (PC3(ADC3))
LED_RED: R8.1, U1.25 (PC2(ADC2))
MISO: J1.1, MAX0.7 (SO), MAX1.7 (SO), MAX2.7 (SO), MAX3.7 (SO), MAX4.7 (SO), MAX5.7 (SO), MAX6.7 (SO), MAX7.7 (SO), U1.16 (PB4(MISO)), U$5.MISO7 (DATA_OUT_MISO)
MOSI: J1.4, U1.15 (PB3(MOSI/OC2)), U$5.MOSI3 (DATA_IN_MOSI)
unnamed: C30.1, MAX0.2 (T-), U$3.2
unnamed: C30.2, MAX0.3 (T+), U$4.2
unnamed: TC0.P$2, U$4.1
unnamed: TC0.P$1, U$3.1
unnamed: LED1.A, R8.2
unnamed: R19.1, U$5.RES8 (DAT2_RES)
unnamed: R18.1, U$5.NC1 (DAT1_NC)
unnamed: C51.1, U1.4 (VCC), U1.6 (VCC)
unnamed: LED2.A, R9.2
unnamed: C31.1, MAX1.2 (T-), U$9.2
unnamed: C31.2, MAX1.3 (T+), U$10.2
unnamed: TC1.P$2, U$10.1
unnamed: TC1.P$1, U$9.1
unnamed: C32.1, MAX2.2 (T-), U$11.2
unnamed: C32.2, MAX2.3 (T+), U$12.2
unnamed: TC2.P$2, U$12.1
unnamed: TC2.P$1, U$11.1
unnamed: C33.1, MAX3.2 (T-), U$13.2
unnamed: C33.2, MAX3.3 (T+), U$14.2
unnamed: TC3.P$2, U$14.1
unnamed: TC3.P$1, U$13.1
unnamed: C34.1, MAX4.2 (T-), U$15.2
unnamed: C34.2, MAX4.3 (T+), U$16.2
unnamed: TC4.P$2, U$16.1
unnamed: TC4.P$1, U$15.1
unnamed: C35.1, MAX5.2 (T-), U$17.2
unnamed: C35.2, MAX5.3 (T+), U$18.2
unnamed: TC5.P$2, U$18.1
unnamed: TC5.P$1, U$17.1
unnamed: C36.1, MAX6.2 (T-), U$19.2
unnamed: C36.2, MAX6.3 (T+), U$20.2
unnamed: TC6.P$2, U$20.1
unnamed: TC6.P$1, U$19.1
unnamed: C37.1, MAX7.2 (T-), U$21.2
unnamed: C37.2, MAX7.3 (T+), U$22.2
unnamed: TC7.P$2, U$22.1
unnamed: TC7.P$1, U$21.1
RESET: C48.2, J1.5, R2.1, RESET_BUTTON.S$1 (S1), U1.29 (PC6(/RESET))
SCK: J1.3, MAX0.5 (SCK), MAX1.5 (SCK), MAX2.5 (SCK), MAX3.5 (SCK), MAX4.5 (SCK), MAX5.5 (SCK), MAX6.5 (SCK), MAX7.5 (SCK), U1.17 (PB5(SCK)), U$5.SCK5 (SCLK)
SCL: DS3231M.8 (P$8_SCL), OLED_0.SCL, OLED_1.SCL, R3.1, U1.28 (PC5(ADC5/SCL))
SDA: DS3231M.7 (P$7_SDA), OLED_0.SDA, OLED_1.SDA, R4.1, U1.27 (PC4(ADC4/SDA))
TO_FTDI_RX: JP1.5, U1.31 (PD1(TXD))
TO_FTDI_TX: JP1.4, U1.30 (PD0(RXD))
VBAT: CR1220_BATTERY.P$1 (VBAT), CR1220_BATTERY.P$2, DS3231M.6 (P$6_VBAT)
VCC: C8.P$1_A (+), C24.+, C40.2, C41.2, C42.2, C43.2, C44.2, C45.2, C46.2, C47.2, C49.1, C51.2, C52.1, DS3231M.2 (P$2_VCC), INDUCTOR.P$2 (2), J1.2, JP1.3, MAX0.4 (VCC), MAX1.4 (VCC), MAX2.4 (VCC), MAX3.4 (VCC), MAX4.4 (VCC), MAX5.4 (VCC), MAX6.4 (VCC), MAX7.4 (VCC), OLED_0.VCC, OLED_1.VCC, R1.2, R2.2, R3.2, R4.2, R10.2, R11.2, R12.2, R13.2, R14.2, R15.2, R16.2, R17.2, R18.2, R19.2, U$5.VDD4 (VDD), U$7.2 (VOUT)
VRAW: C23.+, U$2.P$1 (PWR), U$7.3 (VIN), VIN_KK.2

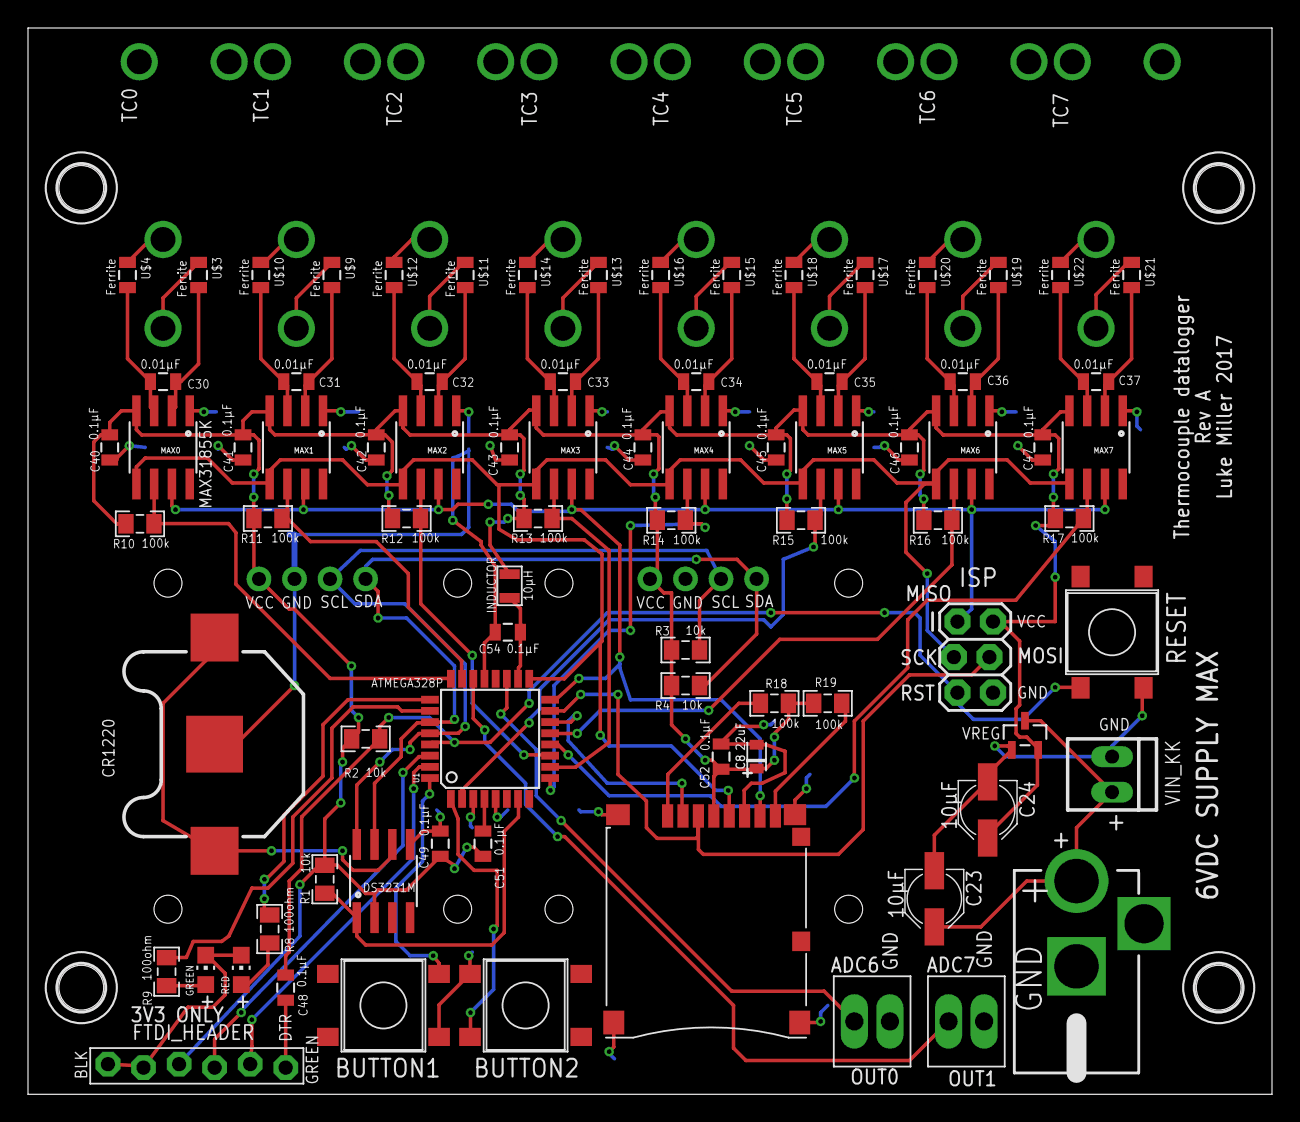
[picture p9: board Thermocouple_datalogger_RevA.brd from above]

Board: 2 copper layers, 88.9 x 76.2 mm, 96 parts (1 on the bottom side), 68 nets.

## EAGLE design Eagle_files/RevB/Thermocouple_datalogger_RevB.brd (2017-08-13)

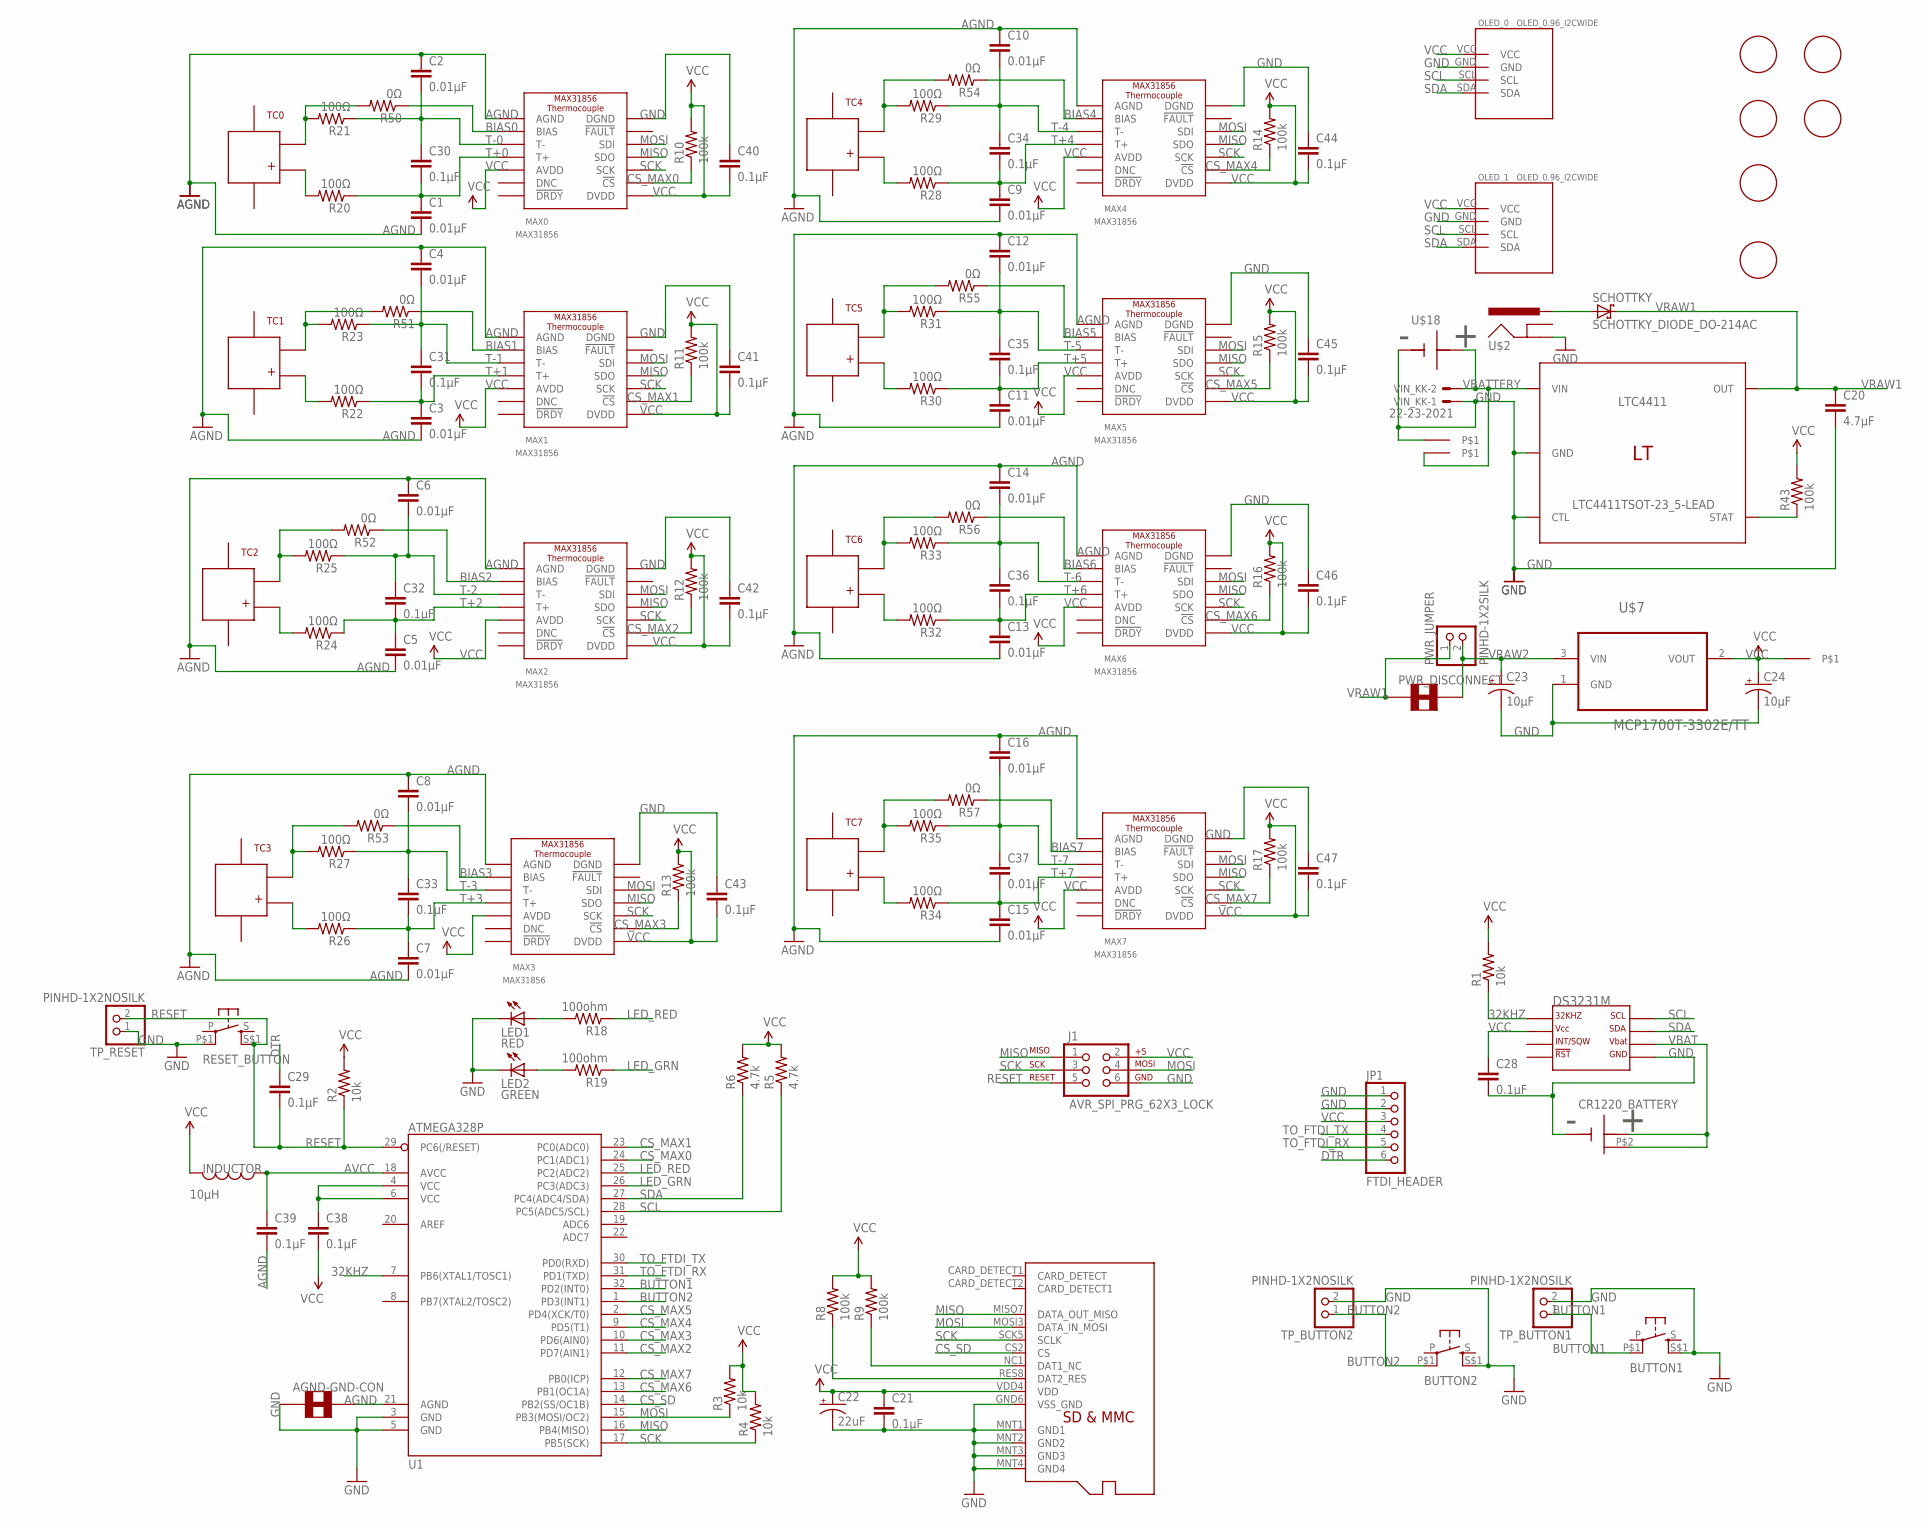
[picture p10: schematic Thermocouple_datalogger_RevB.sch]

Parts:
AGND-GND-CON: SOLDER_JUMPER_TRACESTANDARD; SJ_2S-TRACE
BUTTON1, BUTTON2: PUSHBUTTON_DPST_SMDSTANDARD; PUSHBUTTON_DPST_SMD
C1, C2, C3, C4, C5, C6, C7, C8, C9, C10, C11, C12, C13, C14, C15, C16, C37: 0.01µF; 0805
C20: 4.7µF; 0805
C21, C28, C29, C30, C31, C32, C33, C34, C35, C36, C38, C39, C40, C41, C42, C43, C44, C45, C46, C47: 0.1µF; 0805
C22: 22uF; C0805_POL
C23, C24: 10µF; PANASONIC_B
CR1220_BATTERY: CR1220_BATTERY_HOLDERSMD; CR1220_BATTERY_HOLDER_SMD
DS3231M: DS3231MSOIC-8; DS3231M_SOIC8
INDUCTOR: 10µH; I_0805
J1: AVR_SPI_PRG_62X3_LOCK; 2X3_LOCK
JP1: FTDI_HEADER; 1X06-RIGHT_ANGLE
LED1: RED; CHIPLED_0805
LED2: GREEN; CHIPLED_0805
LTC4411: LTC4411TSOT-23_5-LEAD; TSOT-23_5-LEAD
MAX0, MAX1, MAX2, MAX3, MAX4, MAX5, MAX6, MAX7: MAX31856; MAX31856_TSSOP14
OLED_0, OLED_1: OLED_0.96_I2CWIDE; OLED_0.96_I2C_VCC_PIN1_WIDE
PWR_DISCONNECT: SOLDER_JUMPER_TRACESTANDARD; SJ_2S-TRACE
PWR_JUMPER: PINHD-1X2SILK; 1X02
R1, R2, R3, R4: 10k; R0805
R5, R6: 4.7k; R0805
R8, R9, R10, R11, R12, R13, R14, R15, R16, R17, R43: 100k; R0805
R18, R19: 100ohm; R0805
R20, R21, R22, R23, R24, R25, R26, R27, R28, R29, R30, R31, R32, R33, R34, R35: 100Ω; R0805
R50, R51, R52, R53, R54, R55, R56, R57: 0Ω; R0805
RESET_BUTTON: PUSHBUTTON_SMD; PUSHBUTTON_DPST_SMD
SCHOTTKY: SCHOTTKY_DIODE_DO-214AC; DO214AC
TC0, TC1, TC2, TC3, TC4, TC5, TC6, TC7: PCC-SMP-THERMOCOUPLEVERTICAL; PCC-SMP-V
TP_BUTTON1, TP_BUTTON2: PINHD-1X2NOSILK; 1X02_NOSILK
TP_GND: PINHD-1X1STANDARD; 1X01
TP_RESET: PINHD-1X2NOSILK; 1X02_NOSILK
TP_VBAT: PINHD-1X1STANDARD; 1X01
U1: ATMEGA328P; TQFP32-08
U$2: JACK_2,1MM; POWER_JACK_DC_2,1MM
U$5: MICROSD_MOLEX_REVERSECURRENT; MICROSD_SOCKET_MOLEX_REVERSEMOUNT
U$6, U$15, U$16, U$23, U$24, U$25: HOLE-LAYOUT4-40-SOCKET-HEAD; 4-40-SCREW-HOLE
U$7: MCP1700T-3302E/TT; SOT95P237X112-3N
U$18: BATTERY_4XAA; BATTERY_4XAA_PTH
VCC: PINHD-1X1STANDARD; 1X01
VIN_KK: 22-23-2021

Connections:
32KHZ: DS3231M.1 (P$1_32KHZ), R1.1, U1.7 (PB6(XTAL1/TOSC1))
AGND: AGND-GND-CON.2, C1.2, C2.1, C3.2, C4.1, C5.2, C6.1, C7.2, C8.1, C9.2, C10.1, C11.2, C12.1, C13.2, C14.1, C15.2, C16.1, C39.2, MAX0.AGND, MAX1.AGND, MAX2.AGND, MAX3.AGND, MAX4.AGND, MAX5.AGND, MAX6.AGND, MAX7.AGND, U1.21 (AGND)
AVCC: C39.1, INDUCTOR.P$1 (1), U1.18 (AVCC)
BIAS0: MAX0.BIAS, R50.1
BIAS1: MAX1.BIAS, R51.1
BIAS2: MAX2.BIAS, R52.1
BIAS3: MAX3.BIAS, R53.1
BIAS4: MAX4.BIAS, R54.1
BIAS5: MAX5.BIAS, R55.1
BIAS6: MAX6.BIAS, R56.1
BIAS7: MAX7.BIAS, R57.1
BUTTON1: BUTTON1.P$1 (P1), TP_BUTTON1.1, U1.32 (PD2(INT0))
BUTTON2: BUTTON2.P$1 (P1), TP_BUTTON2.1, U1.1 (PD3(INT1))
CS_MAX0: MAX0.!CS, R10.1, U1.24 (PC1(ADC1))
CS_MAX1: MAX1.!CS, R11.1, U1.23 (PC0(ADC0))
CS_MAX2: MAX2.!CS, R12.1, U1.11 (PD7(AIN1))
CS_MAX3: MAX3.!CS, R13.1, U1.10 (PD6(AIN0))
CS_MAX4: MAX4.!CS, R14.1, U1.9 (PD5(T1))
CS_MAX5: MAX5.!CS, R15.1, U1.2 (PD4(XCK/T0))
CS_MAX6: MAX6.!CS, R16.1, U1.13 (PB1(OC1A))
CS_MAX7: MAX7.!CS, R17.1, U1.12 (PB0(ICP))
CS_SD: U1.14 (PB2(SS/OC1B)), U$5.CS2 (CS)
DTR: C29.1, JP1.6
GND: AGND-GND-CON.1, BUTTON1.S$1 (S1), BUTTON2.S$1 (S1), C20.2, C21.2, C22.P$2_C (-), C23.-, C24.-, C28.2, C40.1, C41.1, C42.1, C43.1, C44.1, C45.1, C46.1, C47.1, CR1220_BATTERY.GND, DS3231M.5 (P$5_GND), J1.6, JP1.1, JP1.2, LED1.C, LED2.C, LTC4411.2 (GND), LTC4411.3 (CTL), MAX0.DGND, MAX1.DGND, MAX2.DGND, MAX3.DGND, MAX4.DGND, MAX5.DGND, MAX6.DGND, MAX7.DGND, OLED_0.GND, OLED_1.GND, RESET_BUTTON.P$1 (P1), TP_BUTTON1.2, TP_BUTTON2.2, TP_GND.1, TP_RESET.1, U1.3 (GND), U1.5 (GND), U$2.P$2 (GND), U$5.GND6 (VSS_GND), U$5.MNT1 (GND1), U$5.MNT2 (GND2), U$5.MNT3 (GND3), U$5.MNT4 (GND4), U$7.1 (GND), U$18.GND, VIN_KK.1
LED_GRN: R19.1, U1.26 (PC3(ADC3))
LED_RED: R18.1, U1.25 (PC2(ADC2))
MISO: J1.1, MAX0.SDO, MAX1.SDO, MAX2.SDO, MAX3.SDO, MAX4.SDO, MAX5.SDO, MAX6.SDO, MAX7.SDO, U1.16 (PB4(MISO)), U$5.MISO7 (DATA_OUT_MISO)
MOSI: J1.4, MAX0.SDI, MAX1.SDI, MAX2.SDI, MAX3.SDI, MAX4.SDI, MAX5.SDI, MAX6.SDI, MAX7.SDI, R3.1, U1.15 (PB3(MOSI/OC2)), U$5.MOSI3 (DATA_IN_MOSI)
unnamed: LTC4411.4 (STAT), R43.1
unnamed: SCHOTTKY.A, U$2.P$1 (PWR)
unnamed: LED1.A, R18.2
unnamed: R8.1, U$5.RES8 (DAT2_RES)
unnamed: R9.1, U$5.NC1 (DAT1_NC)
unnamed: C38.1, U1.4 (VCC), U1.6 (VCC)
unnamed: LED2.A, R19.2
unnamed: R22.2, TC1.P$2
unnamed: R23.2, R51.2, TC1.P$1
unnamed: R24.2, TC2.P$2
unnamed: R25.2, R52.2, TC2.P$1
unnamed: R26.2, TC3.P$2
unnamed: R27.2, R53.2, TC3.P$1
unnamed: R28.2, TC4.P$2
unnamed: R29.2, R54.2, TC4.P$1
unnamed: R30.2, TC5.P$2
unnamed: R31.2, R55.2, TC5.P$1
unnamed: R32.2, TC6.P$2
unnamed: R33.2, R56.2, TC6.P$1
unnamed: R34.2, TC7.P$2
unnamed: R35.2, R57.2, TC7.P$1
RESET: C29.2, J1.5, R2.1, RESET_BUTTON.S$1 (S1), TP_RESET.2, U1.29 (PC6(/RESET))
SCK: J1.3, MAX0.SCK, MAX1.SCK, MAX2.SCK, MAX3.SCK, MAX4.SCK, MAX5.SCK, MAX6.SCK, MAX7.SCK, R4.1, U1.17 (PB5(SCK)), U$5.SCK5 (SCLK)
SCL: DS3231M.8 (P$8_SCL), OLED_0.SCL, OLED_1.SCL, R5.1, U1.28 (PC5(ADC5/SCL))
SDA: DS3231M.7 (P$7_SDA), OLED_0.SDA, OLED_1.SDA, R6.1, U1.27 (PC4(ADC4/SDA))
T+0: C1.1, C30.2, MAX0.T+, R20.1
T+0_TERM: R20.2, TC0.P$2
T+1: C3.1, C31.2, MAX1.T+, R22.1
T+2: C5.1, C32.2, MAX2.T+, R24.1
T+3: C7.1, C33.2, MAX3.T+, R26.1
T+4: C9.1, C34.2, MAX4.T+, R28.1
T+5: C11.1, C35.2, MAX5.T+, R30.1
T+6: C13.1, C36.2, MAX6.T+, R32.1
T+7: C15.1, C37.2, MAX7.T+, R34.1
T-0: C2.2, C30.1, MAX0.T-, R21.1
T-0_TERM: R21.2, R50.2, TC0.P$1
T-1: C4.2, C31.1, MAX1.T-, R23.1
T-2: C6.2, C32.1, MAX2.T-, R25.1
T-3: C8.2, C33.1, MAX3.T-, R27.1
T-4: C10.2, C34.1, MAX4.T-, R29.1
T-5: C12.2, C35.1, MAX5.T-, R31.1
T-6: C14.2, C36.1, MAX6.T-, R33.1
T-7: C16.2, C37.1, MAX7.T-, R35.1
TO_FTDI_RX: JP1.5, U1.31 (PD1(TXD))
TO_FTDI_TX: JP1.4, U1.30 (PD0(RXD))
VBAT: CR1220_BATTERY.P$1 (VBAT), CR1220_BATTERY.P$2, DS3231M.6 (P$6_VBAT)
VBATTERY: LTC4411.1 (VIN), TP_VBAT.1, U$18.VBAT, VIN_KK.2
VCC: C21.1, C22.P$1_A (+), C24.+, C28.1, C38.2, C40.2, C41.2, C42.2, C43.2, C44.2, C45.2, C46.2, C47.2, DS3231M.2 (P$2_VCC), INDUCTOR.P$2 (2), J1.2, JP1.3, MAX0.AVDD, MAX0.DVDD, MAX1.AVDD, MAX1.DVDD, MAX2.AVDD, MAX2.DVDD, MAX3.AVDD, MAX3.DVDD, MAX4.AVDD, MAX4.DVDD, MAX5.AVDD, MAX5.DVDD, MAX6.AVDD, MAX6.DVDD, MAX7.AVDD, MAX7.DVDD, OLED_0.VCC, OLED_1.VCC, R1.2, R2.2, R3.2, R4.2, R5.2, R6.2, R8.2, R9.2, R10.2, R11.2, R12.2, R13.2, R14.2, R15.2, R16.2, R17.2, R43.2, U$5.VDD4 (VDD), U$7.2 (VOUT), VCC.1
VRAW1: C20.1, LTC4411.5 (OUT), PWR_DISCONNECT.1, PWR_JUMPER.1, SCHOTTKY.C
VRAW2: C23.+, PWR_DISCONNECT.2, PWR_JUMPER.2, U$7.3 (VIN)

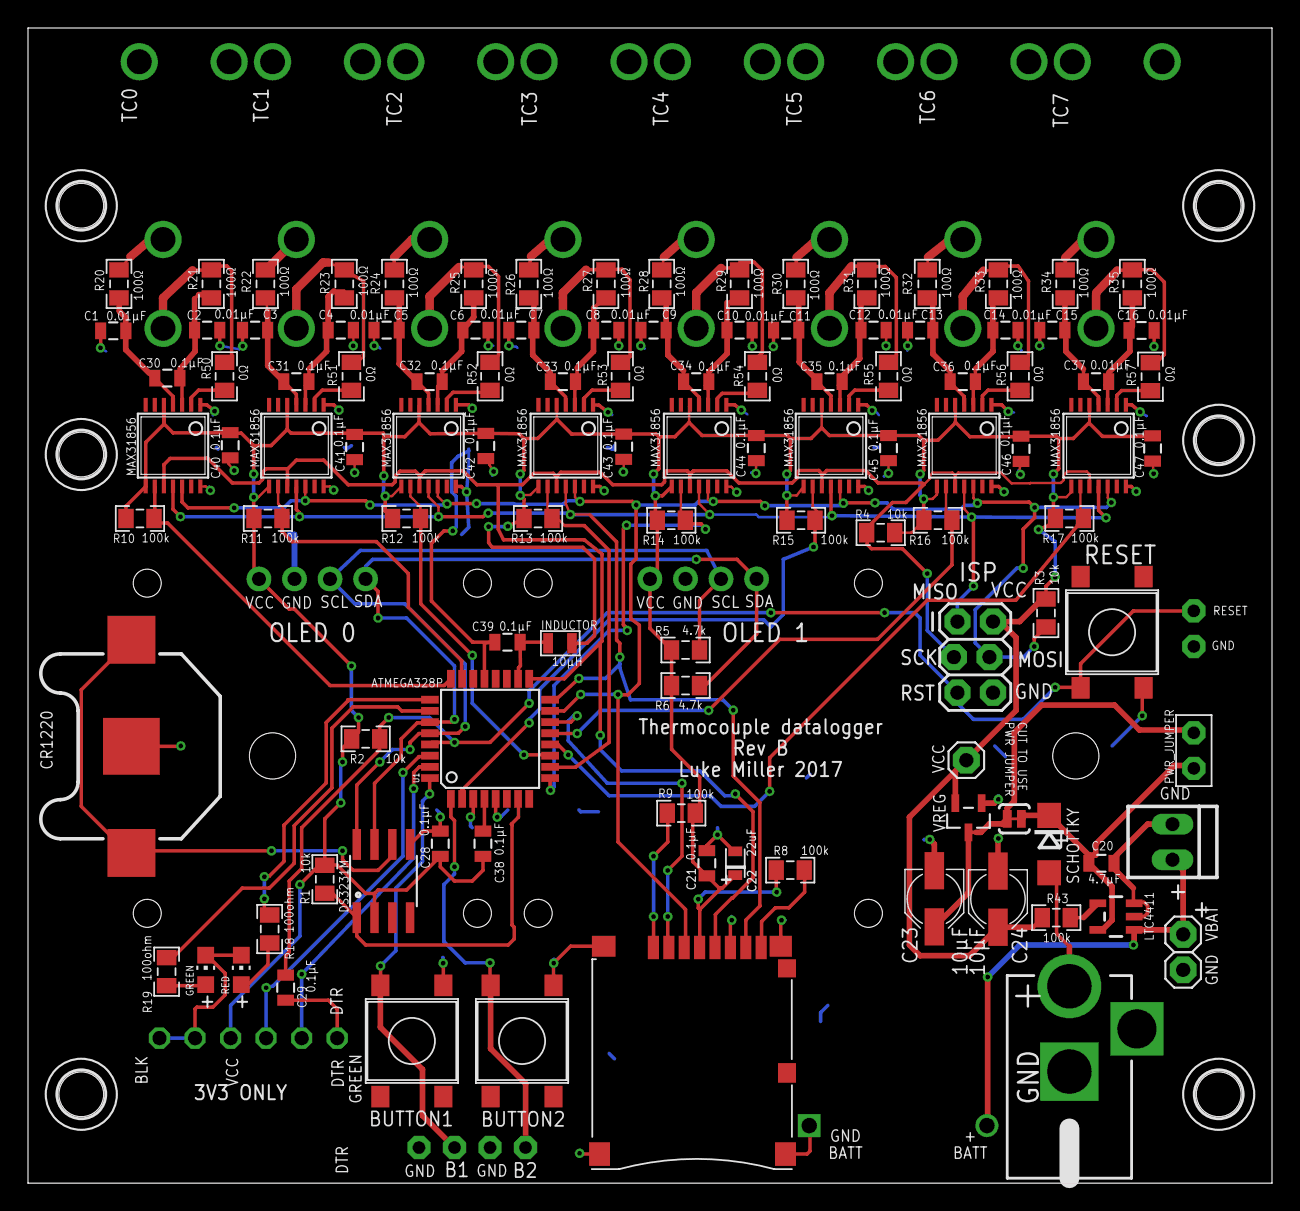
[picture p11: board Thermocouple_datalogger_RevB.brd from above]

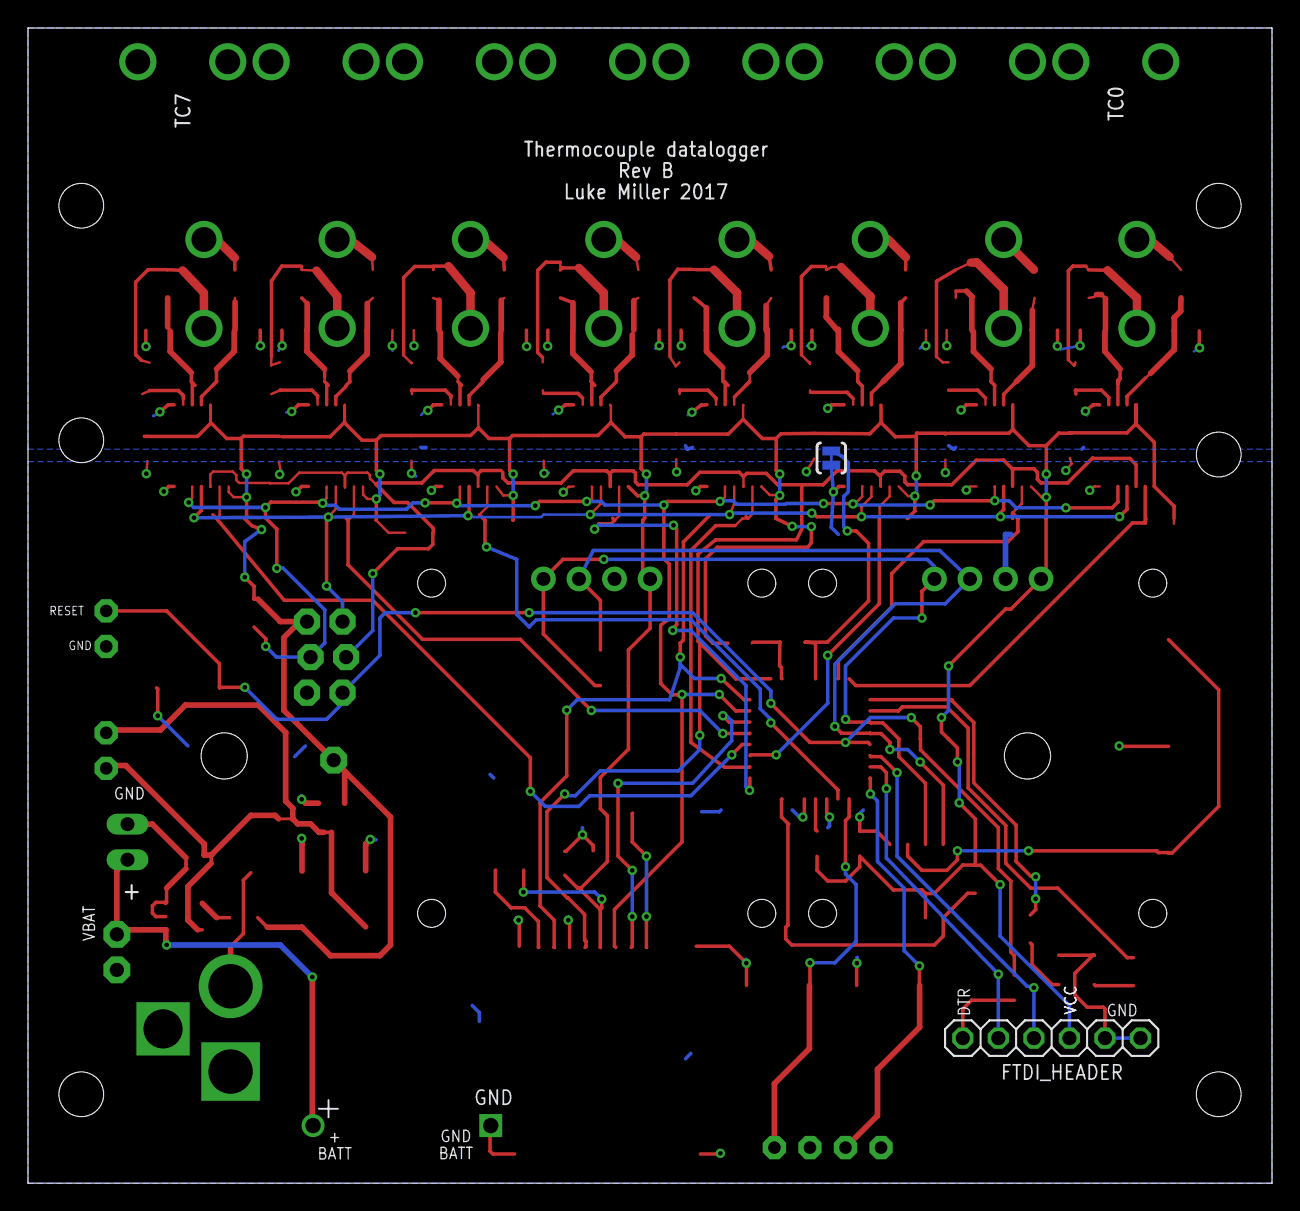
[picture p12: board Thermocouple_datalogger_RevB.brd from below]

Board: 2 copper layers, 88.9 x 82.5 mm, 135 parts (3 on the bottom side), 78 nets.

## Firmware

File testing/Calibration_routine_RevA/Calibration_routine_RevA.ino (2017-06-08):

/*  Calibration_routine.ino
 *   Luke Miller June 2017
 *   
 *   For Thermocouple_datalogger_RevA hardware, this 
 *   program will allow the user to calibrate the 
 *   board's individual MAX31855 thermocouple converter
 *   chips. This requires an external thermocouple
 *   calibrator (see Omega Engineering CL3515R for example)
 *   that can produce a known millivolt signal corresponding
 *   to a certain temperature. 
 *   
 *   The user will use the serial monitor to select
 *   a thermocouple channel to calibrate, and to input
 *   the known temperature value. Output will be
 *   written to csv files, including the known temperature
 *   and recorded temperature.
 * 
 * 
 */

#include "SdFat.h" // https://github.com/greiman/SdFat
#include <Wire.h>  // built in library, for I2C communications
#include <SPI.h>  // built in library, for SPI communications
#include "RTClib.h" // https://github.com/millerlp/RTClib
#include "Adafruit_MAX31855.h" // https://github.com/adafruit/Adafruit-MAX31855-library
#include "TClib2.h" // My utility library for this project

#define ERRLED A2    // Red error LED pin
#define GREENLED A3   // Green LED pin
#define BUTTON1 2     // BUTTON1 on INT0, pin PD2
#define BUTTON2 3     // BUTTON2 on INT1, pin PD3
//*********************
#define SAMPLES 5    // number of samples per temperature
//*********************
// Create real time clock object
RTC_DS3231 rtc;
char buf[20]; // declare a string buffer to hold the time result

//*************
// Create sd card objects
SdFat sd;
//SdFile logfile;  // for sd card, this is the file object to be written to
SdFile calibfile; // for sd card, this is the calibration file to write
const byte chipSelect = 10; // define the Chip Select pin for SD card

// Define MAX31855 objects, need 8 of them for the 8 separate chips
#define CS_MAX0 A1 // Arduino pin PC1, analog 1, Chip Select for MAX31855 #0
#define CS_MAX1 A0 // Arduino pin PC0, analog 0, Chip Select for MAX31855 #1
#define CS_MAX2 7 // Arduino pin PD7, digital 7, Chip Select for MAX31855 #2
#define CS_MAX3 6 // Arduino pin PD6, digital 6, Chip Select for MAX31855 #3
#define CS_MAX4 5 // Arduino pin PD5, digital 5, Chip Select for MAX31855 #4
#define CS_MAX5 4 // Arduino pin PD4, digital 4, Chip Select for MAX31855 #5
#define CS_MAX6 9 // Arduino pin PB1, digital 9, Chip Select for MAX31855 #6
#define CS_MAX7 8 // Arduino pin PB0, digital 8, Chip Select for MAX31855 #7

Adafruit_MAX31855 thermocouple0(CS_MAX0);
Adafruit_MAX31855 thermocouple1(CS_MAX1);
Adafruit_MAX31855 thermocouple2(CS_MAX2);
Adafruit_MAX31855 thermocouple3(CS_MAX3);
Adafruit_MAX31855 thermocouple4(CS_MAX4);
Adafruit_MAX31855 thermocouple5(CS_MAX5);
Adafruit_MAX31855 thermocouple6(CS_MAX6);
Adafruit_MAX31855 thermocouple7(CS_MAX7);
double temp[SAMPLES]; // temperature array

// Define the set of simulated temperatures that will be provided
// by the thermocouple calibrator
byte testTemps[] = {0, 5, 10, 15, 20, 25, 30, 35, 40, 45, 50};
byte tempCounter = 0;

// Declare initial name for output files written to SD card
char calibFilename[] = "YYYYMMDD_HHMM_00_ChX_calib.csv";

byte loopCount = 0; // counter to keep track of data sampling loops
DateTime newtime; // used to track time in main loop
DateTime oldtime; // used to track time in main loop
int Channel;
float targetTemp;
bool continueCalib = true;
char choice;
 
void setup() {
  // Set button1 as an input
  pinMode(BUTTON1, INPUT_PULLUP);
  // Set button2 as an input
  pinMode(BUTTON2, INPUT_PULLUP);
    // Set up the LEDs as output
  pinMode(ERRLED,OUTPUT);
  digitalWrite(ERRLED, LOW);
  pinMode(GREENLED,OUTPUT);
  digitalWrite(GREENLED, LOW);
  // Set the SPI bus chip select pins as outputs
  // for the MAX31855 thermocouple chips
  pinMode(CS_MAX0, OUTPUT);
  digitalWrite(CS_MAX0, HIGH);
  pinMode(CS_MAX1, OUTPUT);
  digitalWrite(CS_MAX1, HIGH);
  pinMode(CS_MAX2, OUTPUT);
  digitalWrite(CS_MAX2, HIGH);
  pinMode(CS_MAX3, OUTPUT);
  digitalWrite(CS_MAX3, HIGH);
  pinMode(CS_MAX4, OUTPUT);
  digitalWrite(CS_MAX4, HIGH);
  pinMode(CS_MAX5, OUTPUT);
  digitalWrite(CS_MAX5, HIGH);
  pinMode(CS_MAX6, OUTPUT);
  digitalWrite(CS_MAX6, HIGH);
  pinMode(CS_MAX7, OUTPUT);
  digitalWrite(CS_MAX7, HIGH);
  // Flash green LED to show that we just booted up
  for (byte i = 0; i < 3; i++){
    digitalWrite(GREENLED, HIGH);
    delay(100);
    digitalWrite(GREENLED, LOW);
    delay(100);
  } 
  Serial.begin(57600);
  Serial.println(F("Hello")); 
//  Serial.println(F("Make sure your terminal is set to No line ending"));

// Initialize the real time clock DS3231M
  Wire.begin(); // Start the I2C library with default options
  rtc.begin();  // Start the rtc object with default options
  newtime = rtc.now(); // read a time from the real time clock
  newtime.toString(buf, 20); 
  printTimeSerial(rtc.now()); // print time to serial monitor
  Serial.println();
  
  delay(1000); 

  //*************************************************************
  // SD card setup and read (assumes Serial output is functional already)
  pinMode(chipSelect, OUTPUT);  // set chip select pin for SD card to output
  // Initialize the SD card object
  // Try SPI_FULL_SPEED, or SPI_HALF_SPEED if full speed produces
  // errors on a breadboard setup. 
  if (!sd.begin(chipSelect, SPI_FULL_SPEED)) {
  // If the above statement returns FALSE after trying to 
  // initialize the card, enter into this section and
  // hold in an infinite loop.
        // There is an error with the SD card, halt everything
    // Consider removing this while loop and allowing user to plow
    // ahead without card (use button input?)
    while(1){ // infinite loop due to SD card initialization error
                        digitalWrite(ERRLED, HIGH);
                        delay(100);
                        digitalWrite(ERRLED, LOW);
                        digitalWrite(GREENLED, HIGH);
                        delay(100);
                        digitalWrite(GREENLED, LOW);
    }
  }
  
  bool channelSelectFlag = false;
  
  while (channelSelectFlag == false){
    Serial.println("Please enter a channel to calibrate (0 to 7):");
    while (!Serial.available());
      if (Serial.available() > 0) {
          // Convert 1st input ascii character to a numeric value (0 to 7)
          Channel = Serial.parseInt();;
          if ( (Channel >= 0) | (Channel <= 7) ){
            Serial.print("Channel ");
            Serial.println(Channel);
            channelSelectFlag = true; // kills while loop
          } else {
            Serial.println("Whoops, please enter value 0 to 7.");
          }
          // Empty the serial buffer
          while (Serial.available() > 0 ){
            char junk = Serial.read();
            delay(5);
          }
      } // end of if (Serial.available() > 0) {
  } // end of while (channelSelectFlag == false)

  // Initialize a new output file
  newtime = rtc.now();
  initCalibFile(newtime, Channel);
  Serial.print(F("Writing to file: "));
  Serial.println(calibFilename);
  
  
    
} // end of setup() loop

//************************************************
void loop() {
  
  while (continueCalib & (tempCounter < (sizeof(testTemps)/sizeof(byte)))){
    Serial.print(F("Set calibrator to "));
    Serial.print(testTemps[tempCounter]);
    Serial.println(F(" C, and hit enter to start"));
    
    while  (Serial.available()<=0) {}; // wait for user response
    if (Serial.available() > 0){
      // Empty the serial buffer
      while (Serial.available() > 0 ){
        char junk = Serial.read();
        Serial.println(junk);
        delay(5);
      }
      // Get next test temperature
      targetTemp = testTemps[tempCounter];
      Serial.print(F("Target temperature: \t"));
      Serial.print(targetTemp);
      Serial.println(F(" C"));
    }
    // Now read appropriate channel
    switch(Channel){
      case 0:
        for (int i = 0; i < SAMPLES; i++){
          temp[i] = thermocouple0.readCelsius();
          Serial.print(targetTemp);
          Serial.print(F("\t"));
          Serial.println(temp[i]);
          delay(500);         
        }
      break;
      case 1:
        for (int i = 0; i < SAMPLES; i++){
          temp[i] = thermocouple1.readCelsius();
          Serial.print(targetTemp);
          Serial.print(F("\t"));
          Serial.println(temp[i]);
          delay(500);         
        }
      break;
      case 2:
        for (int i = 0; i < SAMPLES; i++){
          temp[i] = thermocouple2.readCelsius();
          Serial.print(targetTemp);
          Serial.print(F("\t"));
          Serial.println(temp[i]);
          delay(500);         
        }
      break; 
      case 3:
        for (int i = 0; i < SAMPLES; i++){
          temp[i] = thermocouple3.readCelsius();
          Serial.print(targetTemp);
          Serial.print(F("\t"));
          Serial.println(temp[i]);
          delay(500);         
        }
      break;
      case 4:
        for (int i = 0; i < SAMPLES; i++){
          temp[i] = thermocouple4.readCelsius();
          Serial.print(targetTemp);
          Serial.print(F("\t"));
          Serial.println(temp[i]);
          delay(500);         
        }
      break;
      case 5:
        for (int i = 0; i < SAMPLES; i++){
          temp[i] = thermocouple5.readCelsius();
          Serial.print(targetTemp);
          Serial.print(F("\t"));
          Serial.println(temp[i]);
          delay(500);         
        }
      break;
      case 6:
        for (int i = 0; i < SAMPLES; i++){
          temp[i] = thermocouple6.readCelsius();
          Serial.print(targetTemp);
          Serial.print(F("\t"));
          Serial.println(temp[i]);
          delay(500);         
        }
      break;
      case 7:
        for (int i = 0; i < SAMPLES; i++){
          temp[i] = thermocouple7.readCelsius();
          Serial.print(targetTemp);
          Serial.print(F("\t"));
          Serial.println(temp[i]);
          delay(500);         
        }
      break;                                       
    }
    // Write temp array to SD card
    writeCalibSD(targetTemp,temp);
    // Increment tempCounter
    ++tempCounter;

//    while (Serial.read() >= 0) {};
//    // Finished taking data, ask user to continue or quit
//    Serial.println(F("Continue or quit? y or q: "));
//    while (!Serial.available()) ; // wait for response
//    if (Serial.available() > 0 ) {
//        choice = Serial.read();
//       if (choice == 'y'){
//          continueCalib = true;
//       } else if (choice == 'q') {
//          continueCalib = false; // kill this inner loop
//       }
//    }
//    while (Serial.read() >= 0) {}; // flush out buffer
    
  } // end of while (continueCalib)
    // The while loop above should end when the last
    // temperature has been run, so finish by closing 
    // the SD card file. 

//  if (!continueCalib){
    // Clean up and go into suspension
    calibfile.close();
    Serial.print(F("Saved file: "));
    Serial.println(calibFilename);
    Serial.println(F("Reset to calibrate again"));
    while(1); // infinite loop  
//  }
  

} // end of main loop()


//---------writeCalibSD-----------------------
// A function to write the current targetTemp and temperature to the 
// csv file
void writeCalibSD (float targetTemp, double *temp){
    // Reopen logfile. If opening fails, notify the user
  if (!calibfile.isOpen()) {
    if (!calibfile.open(calibFilename, O_RDWR | O_CREAT | O_AT_END)) {
      digitalWrite(ERRLED, HIGH); // turn on error LED
    }
  }
  for (int i = 0; i < SAMPLES; i++){
    calibfile.print(targetTemp); // repeat this for each entry
    calibfile.print(F(","));
    calibfile.print(temp[i]);     
    calibfile.print(F(","));
    calibfile.println(Channel);
  }
}
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

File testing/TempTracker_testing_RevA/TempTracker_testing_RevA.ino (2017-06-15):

/* TempTracker_testing.ino
	Copyright Luke Miller 2017

  TODO: implement error handling on RTC and SD card, to allow usage without
  full functionality
  TODO: Implement screen power down and button to wake screens
  
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
  Code to run a Thermocouple_datalogger_RevA board with
  MAX31855 thermocouple sensors. By default
  this program will start running and saving data to the SD 
  card automatically. 
  	
	Closing a data file safely:
		1. Hold button 1 down for at least 7 seconds, then release it.
		2. The green LED should flash rapidly 15 times. The previous data
			file will be closed safely, and a new file will be started in
			normal data collection mode. 
  
	Board error codes:
		Red flashes quickly (10Hz): Real Time Clock not set
		Red + Green alternate rapidly: SD card not found
                Red permanently on: SD card not found after data collection started
		Red flash every ~8 seconds: In brownout mode, data collection has stopped

*/

#include "SdFat.h" // https://github.com/greiman/SdFat
#include <Wire.h>	// built in library, for I2C communications
#include "SSD1306Ascii.h" // https://github.com/greiman/SSD1306Ascii
#include "SSD1306AsciiWire.h" // https://github.com/greiman/SSD1306Ascii
#include <SPI.h>	// built in library, for SPI communications
#include "RTClib.h" // https://github.com/millerlp/RTClib
#include "MAX31855K_NIST.h" // https://github.com/millerlp/MAX31855K_NIST
#include "TClib2.h" // My utility library for this project

// Various additional libraries for access to sleep mode functions
#include <avr/interrupt.h>
#include <avr/sleep.h>
#include <util/atomic.h>
#include <wiring_private.h>
#include <avr/wdt.h>
//******************************
// Data collection rate, enter a value here of 4, 2, or 1 (samples per second)
#define SAMPLES_PER_SECOND 2 // number of samples taken per second (4, 2, or 1)
//******************************
// Define the number of samples per sensor to average (moving average window)
#define AVG_WINDOW 4  // Just a number, no units
// Define the interval (seconds) between saved values (writing to SD card)
#define SAVE_INTERVAL 5 // units of seconds

//********************************
// tcOffset array contains individual calibration adjustments for each
// of the 8 MAX31855K chips on the board being programmed. tcSlope contains
// calibration slope adjustments in the same manner. These values 
// will have been determined with the help of the Calibration_routine_OLED.ino
// program and an external thermocouple calibrator such as an Omega CL3515R.
// The values were generated from a linear regression fit through the sensor
// temperatures and the known calibrator temperatures. 

// Values for RevA1 board 1, calibrated on 2017-06-15
//                      Ch0         Ch1       Ch2         Ch3       Ch4         Ch5       Ch6         Ch7                  
double tcOffset[] = {-0.2352983, 0.2763315,-0.2781568, 0.5066493, 0.1212014, 0.3781640,-0.1821470,-0.4756476}; 
double tcSlope[] =  { 1.0027047, 0.9999684, 1.0021402, 1.0017356, 1.0011395, 1.0018918, 1.0018701, 1.0016286};
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

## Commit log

2017-06-05 Functional test prototype with 2 OLED screens, RTC, buttons etc.
2017-06-06 Non-tested, probably not functional prototype program
2017-06-06 Mostly functional basic datalogger
    TODOs: implement button functions, sleep screens, refine screen refresh,
    implement moving average of temperatures
2017-06-06 Currently appears functional. Added separate data saving interval and sampling interval, with moving average window
2017-06-07 Resolving last conflict, functional prototype now
2017-06-08 Adding calibration program
2017-06-08 Updated routine to just automatically set next test temperature
2017-06-08 Switched to all onboard control
    Uses the buttons and OLED screens to let the user calibrate, without the
    need for a serial connection.
2017-06-14 Adding temperature output to wait screen, and internal temperature on wait screen as well.
2017-06-14 Adding in code to use NIST-corrected temperature output from the MAX31855 chips. Saved data now reflect this corrected value rather than the raw temperature value coming directly from the MAX31855.
2017-06-15 Switching over to using MAX31855K_NIST library
    The new library makes use of simultaneously measured internal and
    external temperatures of the MAX31855K and implements a linearization
    using the NIST K-type polynomial and coefficients.
2017-06-15 Adding in calibration offsets for all 8 channels, based on calibrations carried out on 2017-06-14 and 15 with RevA Board 1.
2017-06-15 Applying calibration corrections to the incoming temperature values individually, using pooled calibration data coefficients.
2017-06-15 Functional data collection routine, with calibration coefficients.
2017-08-11 Currently having problems, registering no MAX31856
    There's some kind of issue with the MAX31856, possibly because the SdFat
    library is also trying to use the SPI lines now?
2017-08-11 First test, works fine for one channel on RevB board
2017-08-12 Basic working calibration routine with 8 channels
2017-08-12 Program to store individual MAX31856 calibration slope and offset values in the board's EEPROM memory
2017-08-12 Testing code to read/write calibration values from EEPROM
2017-08-12 Adding routing to read calibration offset and slope values from EEPROM at startup, or use default values (0.00, 1.00) if none are present in EEPROM.
2017-08-13 Adding sanity checking to the EEPROM values
    Calibration values read out from the EEPROM should be sanity checked to
    make sure they are within semi-reasonable bounds. The offset (intercept)
    value may deviate a couple of degrees from the factory, so we set a wide
    range of +/- 3. The slope range is restricted to 0.5 to 1.5 by this
    code, and we really ought to expect a slope very close to 1.0. If
    calibrations values are outside these bounds, either the EEPROM values
    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
2017-08-13 Updating to read calibration from EEPROM
    Use the separate program Store_calibrations.ino to write the 8 channel
    calibration slope + offset values into EEPROM for a particular board.
    This modification will then read those values out of EEPROM and use
    them. This removes the need to alter this main program every time you
    want to program a different board that has its own calibration
    coefficients.
2017-08-13 Moving Serial print messages to PROGMEM
2017-08-13 Moving board design files over
    [Thermocouple_datalogger_RevA.brd, Thermocouple_datalogger_RevA.sch, Thermocouple_datalogger_RevA_bom.csv, Thermocouple_datalogger_RevB.brd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]
2017-08-13 Adding board picture
2017-08-22 Writing a little test program to make sure math and calibrations are being applied properly
2017-08-22 Cleaning out older cruft, adding in a new column of output data holding cold junction temperatures
2017-08-22 Making the loop end at NUM_MAX31856 instead of hard-coded 8, also printing more digits for the calibration coefficient readout
2023-03-15 Removing Button 2, but this didn't fix things with the busted board
2024-02-16 Updating time printout via toString() function
    RTClib changed a while back, and the toString() function changed as a result, so this should fix the various places where it's used to print out the date and time.

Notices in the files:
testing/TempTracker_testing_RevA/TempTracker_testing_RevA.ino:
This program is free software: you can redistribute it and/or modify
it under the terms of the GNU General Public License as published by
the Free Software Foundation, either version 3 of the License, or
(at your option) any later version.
